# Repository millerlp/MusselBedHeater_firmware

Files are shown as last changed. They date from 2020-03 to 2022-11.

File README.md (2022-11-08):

# MusselBedHeater_firmware
Luke Miller, 2020

A permanent archive of this repository is stored in a Zenodo archive: https://doi.org/10.5281/zenodo.7246441 

 Firmware and hardware for Mussel Bed Heater project that Claire Windecker carried out 
 for her Masters thesis at Cal Poly Humboldt. The project consists of a circuit board 
 design that uses Arduino software to control an ATmega328P microcontroller to carry out 
 temperature monitoring and control heated artificial mussel beds. 
 
MusselBedHeater circuit board diagram

## Hardware design files 

Hardware_files/ contains parts lists, bill of materials, and Autocad Eagle design files. MusselBedHeater_RevG is the
most recent version, and contains all of the modifications made to the Revision F boards that were used 
in the field experiment. The heater sub-assembly board is in Heater_subassembly_revA.

## Arduino software files 

library_copies/ contains copies of the necessary Arduino libraries used to run the MusselBedHeater_firmware

Arduino programs used to run the hardware in the field are contained in:
* MusselBedHeater_6Crise/
* MusselBedHeater_field/

Utility Arduino programs used to set up the boards initially are in:
* serial_number_generator/
* settime_Serial/

### Reference mussels

Part of the design included the need to have a reference temperature, which the heated mussels would then 
be heated above by 2C or 6C. Reference mussels used a MAX31820 OneWire temperature sensor, which was 
embedded in artificial epoxy mussels as well. One control board can monitor 4 reference temperature sensors. 
The software averages the temperatures from the available reference mussels and uses that value to establish
the 'ambient' mussel temperature. Heated mussels were then heated to a target temperature increase, 2 or 6 degrees
Celsius above ambient. 

A TO-92 package MAX31820 is shown wired into the cable that will lead back to the battery box and controller board.
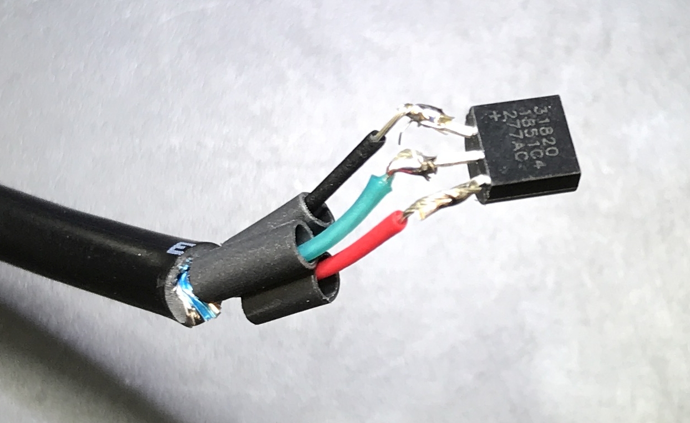
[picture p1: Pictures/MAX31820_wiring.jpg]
MAX31820 sensor wiring


## Heating assembly 

The heated artificial mussels were built using 38 Gauge Nichrome 80 wire (14 ohm per meter) in a 
length of 300 mm (~12 inches) wrapped around the Heater_subassembly_revA circuit board. This arrangement
should consume a maximum of about 3 Watts at 13V supply, but the circuit board is designed to pulse width
modulate the supply voltage to the heater and provide a basic PID control algorithm to achieve a desired 
target temperature above ambient. 

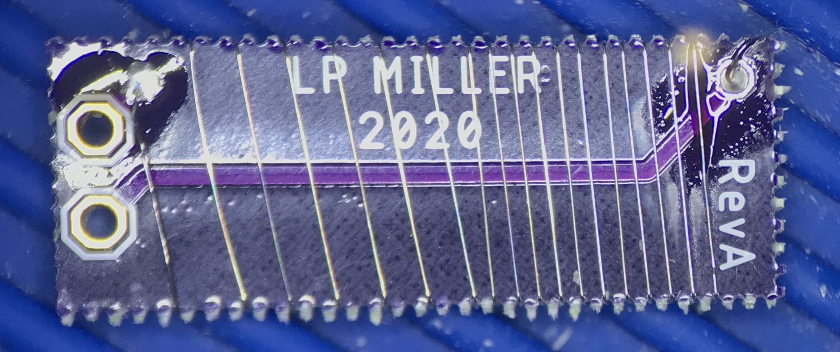
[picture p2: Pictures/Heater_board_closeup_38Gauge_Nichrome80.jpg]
Subassembly board


The cable supplying power to the heater coil also connected to a 6800 ohm 3% NTC thermistor, which was
used to measure the temperature of the artificial mussel. The thermistor was wired in a half-bridge
configured with 4700 ohm precision resistors found on the main MusselBedHeater_RevG circuit board.

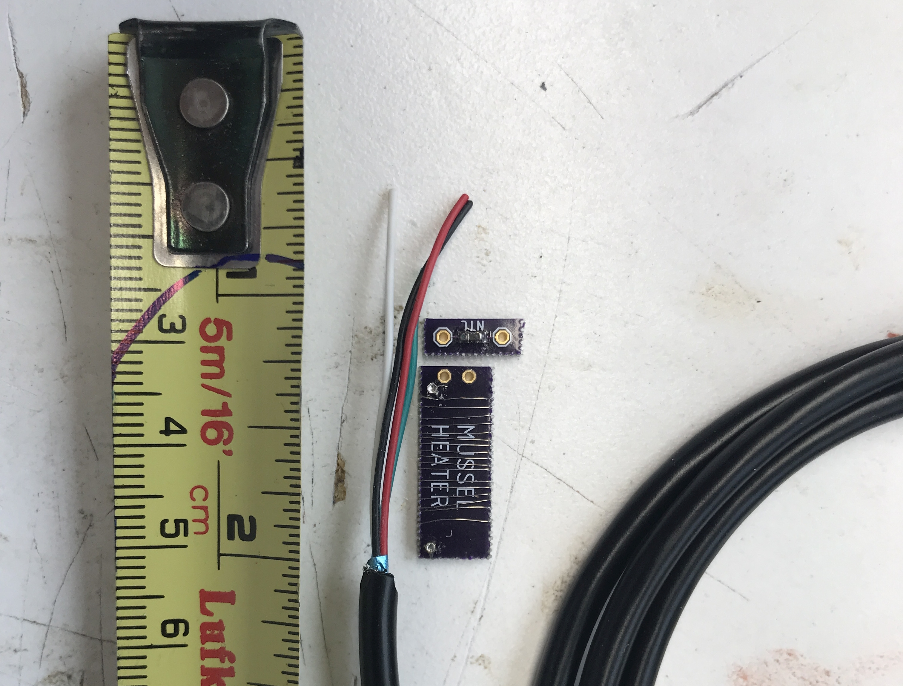
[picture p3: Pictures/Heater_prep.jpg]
Thermistor and heater coil board


The thermistor and heater coil board were eventually cast into the middle of an epoxy artificial mussel. 

One control board can control up to 16 heated mussels, including measuring their thermistor temperatures.

## Acknowledgements 
Funding from the National Science Foundation grants OCE-1904184 and OCE-1904185 helped support Luke Miller 
during the development of this hardware and software.

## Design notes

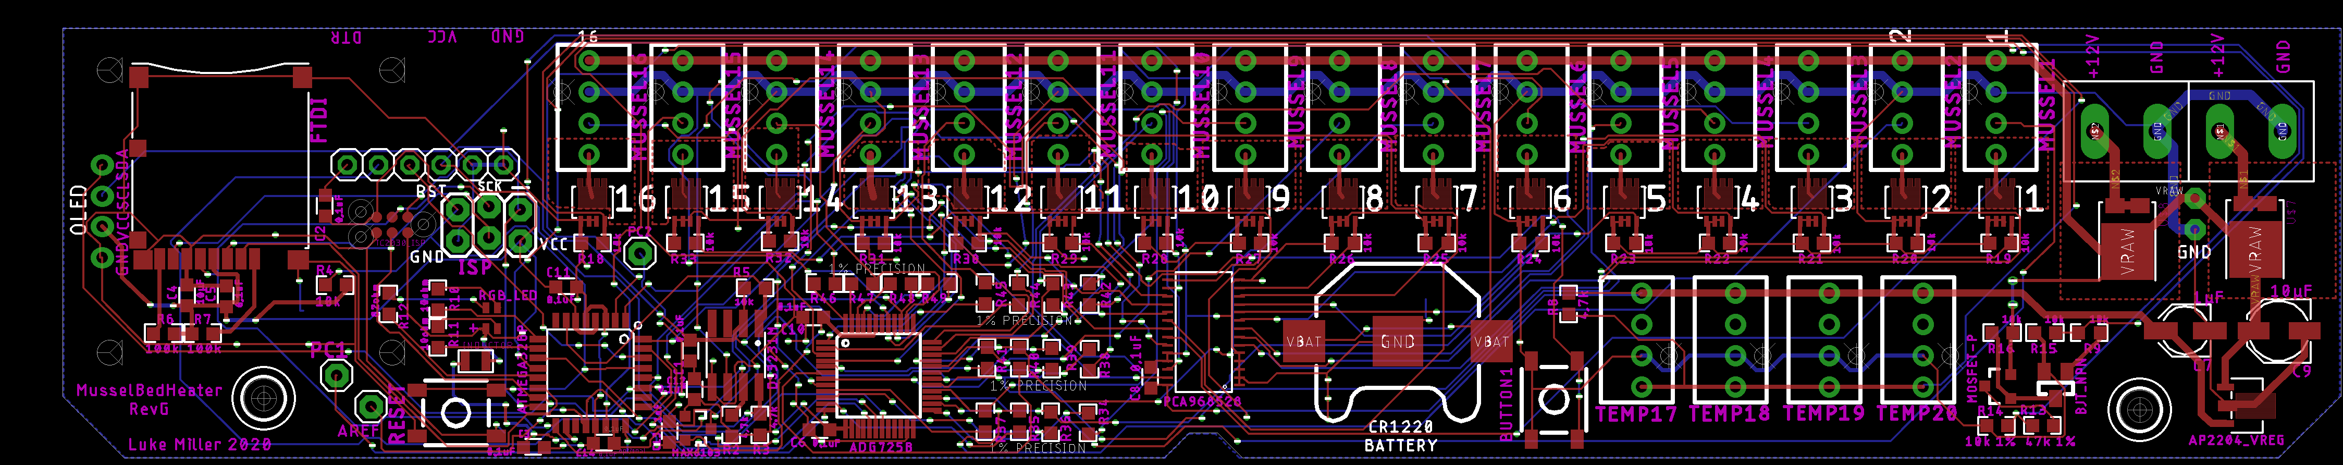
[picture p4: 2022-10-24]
Hardware_files/Eagle_files/MusselBedHeater_RevG_board.png

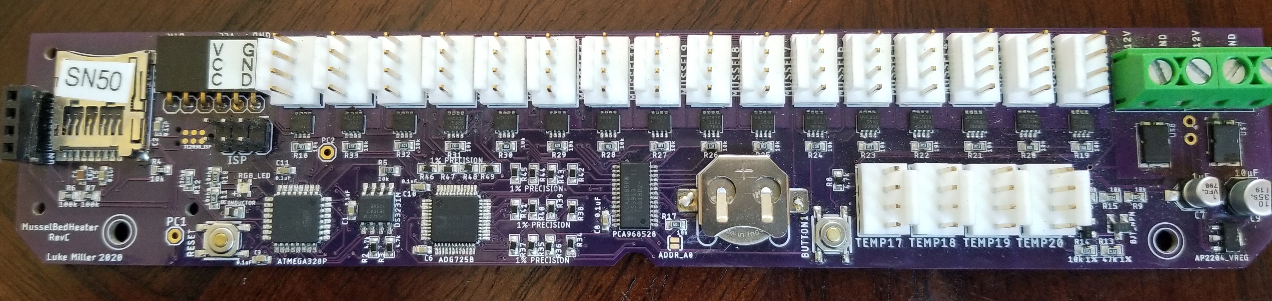
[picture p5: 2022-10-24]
Pictures/20210609_122934_RevE.jpg

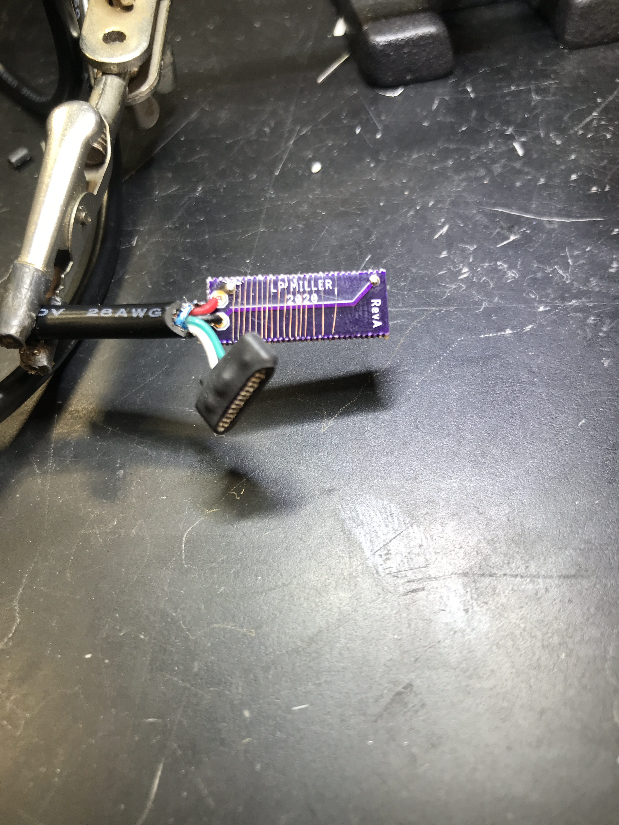
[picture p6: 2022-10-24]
Pictures/Heater_and_thermistor_finished.jpg

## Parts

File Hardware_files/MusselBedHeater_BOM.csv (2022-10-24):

Revision F, G MusselBedHeater
Qty | Value | Device | Package | Parts
1 |  | PINHD-1X6RA | 1X06-RIGHT_ANGLE | FTDI
10 | 0.1uF | CAP0603 | 0603 | C1, C2, C3, C5, C6, C8, C10, C11, C12, C14
2 | 100k 5% | RESISTOR_SMDR0603 | R0603 | R6, R7
21 | 10k 5% | RESISTOR_SMDR0603 | R0603 | R4, R5, R9, R15, R16, R18, R19, R20, R21, R22, R23, R24, R25, R26, R27, R28, R29, R30, R31, R32, R33
1 | 10k 1% or 0.5% | RESISTOR_SMDR0603 (battery reference) | R0603 | R14
2 | 10 ohm | RESISTOR_SMDR0603 (LED) | R0603 | R10, R11
1 | 10 µF | CAP0603 | 0603 | C4
1 | 10 µF | CPOL-USC | PANASONIC_C | C9
1 | 1uF | CAP0603 | 0603 | C13
1 | 1µF | CPOL-USB | PANASONIC_B | C7
3 | 4.7k 5% | RESISTOR_SMDR0603 (pull-ups) | R0603 | R2, R3, R8
16 | 4.7 kohm 1% | RESISTOR_SMDR0603 (thermistor ref) | R0603 | R34, R35, R36, R37, R38, R39, R40, R41, R42, R43, R44, R45, R46, R47, R48, R49
1 | 47k 1% or 0.5% | RESISTOR_SMDR0603 (battery reference) | R0603 | R13
1 | 82 ohm | RESISTOR_SMDR0603 (LED) | R0603 | R12
1 | ADG725_MUX | ADG725_MUX | TQFP48 | ADG725B
1 | AP2204R | AP2204R Voltage regulator | SOT-89 | AP2204_VREG
1 | ATMEGA328P | ATMEGA328_SMT | TQFP32-08 | ATMEGA328P
1 | AVR_SPI_PRG_62X3_LOCK | 2x3 header 0.1" pitch | 2X3_LOCK | ISP
1 | BATTERY_BUTTON_CELLCR1220_SMD | BATTERY_BUTTON_CELLCR1220_SMD | CR1220_BATTERY_HOLDER_SMD | U$5
1 | BJT_NPN_FMMT619TA | BJT_NPN_FMMT619TA (battery monitor) | SOT23 | BJT_NPN
1 | MOSFET-PCHANNELBSH203 | MOSFET-PCHANNELBSH203 (battery monitor) | SOT23-3 | MOSFET-P
1 | DS3231MSOIC-8 | DS3231MSOIC-8 (real time clock) | DS3231M_SOIC8 | DS3231M
1 | INDUCTOR0805_TY | INDUCTOR0805_TY | I_0805 | INDUCTOR
1 | LED_3_COLOR_ANODE1 | LED_3_COLOR_ANODE1 | LED_RGB_SMD_1.6X1.6 | RGB_LED
1 | MAX6100-MAX6107_VOLTAGE_REF | MAX6100-MAX6107_VOLTAGE_REF | SOT23-3 | MAX6103
1 | MICROSD_MOLEX_REVERSECURRENT | MICROSD_MOLEX_REVERSECURRENT | MICROSD_SOCKET_MOLEX_REVERSEMOUNT | U$2
16 | MOSFET-N_LFPAK33 | MOSFET-N_LFPAK33 | SOT1210 | U$10, U$11, U$12, U$13, U$14, U$15, U$16, U$17, U$18, U$19, U$20, U$21, U$22, U$23, U$24, U$25
1 | OLED_0.96_I2CGND_PIN1_WIDE | 4-pin 0.1" pitch header | OLED_0.96_I2C_GND_PIN1_WIDE | OLED
1 | PCA968528 | PCA968528 | 28-TSSOP | PCA9685
2 | PUSHBUTTON_DPST_SMD2SMALL | PUSHBUTTON_DPST_SMD2SMALL | PUSHBUTTON_SPST_PTS525_SERIES | BUTTON1, RESET
2 | SCHOTTKY_DIODE_TO-277-3 | SCHOTTKY_DIODE_TO-277-3 | TO-277-3 | U$7, U$8
2 | TERMINAL-2PIN-5.08MMLARGEHOLE | TERMINAL-2PIN-5.08MMLARGEHOLE | TERMINAL-2PIN-5.08MM_LARGEHOLE | BATT_INPUT1, BATT_INPUT2

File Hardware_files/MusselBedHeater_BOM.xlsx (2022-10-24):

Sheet: RevF-G
Revision F, G MusselBedHeater
Qty | Value | Device | Package | Parts
1 |  | PINHD-1X6RA | 1X06-RIGHT_ANGLE | FTDI
10 | 0.1uF | CAP0603 | 0603 | C1, C2, C3, C5, C6, C8, C10, C11, C12, C14
2 | 100k 5% | RESISTOR_SMDR0603 | R0603 | R6, R7
21 | 10k 5% | RESISTOR_SMDR0603 | R0603 | R4, R5, R9, R15, R16, R18, R19, R20, R21, R22, R23, R24, R25, R26, R27, R28, R29, R30, R31, R32, R33
1 | 10k 1% or 0.5% | RESISTOR_SMDR0603 (battery reference) | R0603 | R14
2 | 10 ohm | RESISTOR_SMDR0603 (LED) | R0603 | R10, R11
1 | 10 µF | CAP0603 | 0603 | C4
1 | 10 µF | CPOL-USC | PANASONIC_C | C9
1 | 1uF | CAP0603 | 0603 | C13
1 | 1µF | CPOL-USB | PANASONIC_B | C7
3 | 4.7k 5% | RESISTOR_SMDR0603 (pull-ups) | R0603 | R2, R3, R8
16 | 4.7 kohm 1% | RESISTOR_SMDR0603 (thermistor ref) | R0603 | R34, R35, R36, R37, R38, R39, R40, R41, R42, R43, R44, R45, R46, R47, R48, R49
1 | 47k 1% or 0.5% | RESISTOR_SMDR0603 (battery reference) | R0603 | R13
1 | 82 ohm | RESISTOR_SMDR0603 (LED) | R0603 | R12
1 | ADG725_MUX | ADG725_MUX | TQFP48 | ADG725B
1 | AP2204R | AP2204R Voltage regulator | SOT-89 | AP2204_VREG
1 | ATMEGA328P | ATMEGA328_SMT | TQFP32-08 | ATMEGA328P
1 | AVR_SPI_PRG_62X3_LOCK | 2x3 header 0.1" pitch | 2X3_LOCK | ISP
1 | BATTERY_BUTTON_CELLCR1220_SMD | BATTERY_BUTTON_CELLCR1220_SMD | CR1220_BATTERY_HOLDER_SMD | U$5
1 | BJT_NPN_FMMT619TA | BJT_NPN_FMMT619TA (battery monitor) | SOT23 | BJT_NPN
1 | MOSFET-PCHANNELBSH203 | MOSFET-PCHANNELBSH203 (battery monitor) | SOT23-3 | MOSFET-P
1 | DS3231MSOIC-8 | DS3231MSOIC-8 (real time clock) | DS3231M_SOIC8 | DS3231M
1 | INDUCTOR0805_TY | INDUCTOR0805_TY | I_0805 | INDUCTOR
1 | LED_3_COLOR_ANODE1 | LED_3_COLOR_ANODE1 | LED_RGB_SMD_1.6X1.6 | RGB_LED
1 | MAX6100-MAX6107_VOLTAGE_REF | MAX6100-MAX6107_VOLTAGE_REF | SOT23-3 | MAX6103
1 | MICROSD_MOLEX_REVERSECURRENT | MICROSD_MOLEX_REVERSECURRENT | MICROSD_SOCKET_MOLEX_REVERSEMOUNT | U$2
16 | MOSFET-N_LFPAK33 | MOSFET-N_LFPAK33 | SOT1210 | U$10, U$11, U$12, U$13, U$14, U$15, U$16, U$17, U$18, U$19, U$20, U$21, U$22, U$23, U$24, U$25
1 | OLED_0.96_I2CGND_PIN1_WIDE | 4-pin 0.1" pitch header | OLED_0.96_I2C_GND_PIN1_WIDE | OLED
1 | PCA968528 | PCA968528 | 28-TSSOP | PCA9685
2 | PUSHBUTTON_DPST_SMD2SMALL | PUSHBUTTON_DPST_SMD2SMALL | PUSHBUTTON_SPST_PTS525_SERIES | BUTTON1, RESET
2 | SCHOTTKY_DIODE_TO-277-3 | SCHOTTKY_DIODE_TO-277-3 | TO-277-3 | U$7, U$8
2 | TERMINAL-2PIN-5.08MMLARGEHOLE | TERMINAL-2PIN-5.08MMLARGEHOLE | TERMINAL-2PIN-5.08MM_LARGEHOLE | BATT_INPUT1, BATT_INPUT2

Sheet: RevC
Exported from MusselBedHeater_RevC.sch 2020-03-09
Qty | Value | Device | Package | Parts
1 | Right angle 1x6 header | PINHD-1X6RA | 1X06-RIGHT_ANGLE | FTDI
2 | 100k 5% | RESISTOR_SMDR0603 | R0603 | R6, R7
22 | 10k 5% | RESISTOR_SMDR0603 | R0603 | R4, R5, R9, R15, R16, R17, R18, R19, R20, R21, R22, R23, R24, R25, R26, R27, R28, R29, R30, R31, R32, R33
1 | 10k 1% | RESISTOR_SMDR0603 | R0603 | R14
2 | 10ohm 5% | RESISTOR_SMDR0603 | R0603 | R10, R11
1 | 82ohm 5% | RESISTOR_SMDR0603 | R0603 | R12
8 | 0.1uF | CAP0603 | 603 | C1, C2, C3, C5, C6, C8, C10, C11
1 | 10µF | CAP0603 | 603 | C4
1 | 10µF | CPOL-USC | PANASONIC_C | C9
1 | 1µF | CPOL-USB | PANASONIC_B | C7
3 | 4.7k 5% | RESISTOR_SMDR0603 | R0603 | R2, R3, R8
16 | Rref_1% (4.7kohm) | RESISTOR_SMDR0603 | R0603 | R34, R35, R36, R37, R38, R39, R40, R41, R42, R43, R44, R45, R46, R47, R48, R49
1 | 47k 1% | RESISTOR_SMDR0603 | R0603 | R13
1 | ADG725_MUX | ADG725_MUX | TQFP48 | ADG725B
1 | AP2204R | AP2204R | SOT-89 | AP2204_VREG
1 | ATMEGA328P | ATMEGA328_SMT | TQFP32-08 | ATMEGA328P
1 | AVR_SPI_PRG_62X3_LOCK | AVR_SPI_PRG_62X3_LOCK | 2X3_LOCK | ISP
1 | BATTERY_BUTTON_CELLCR1220_SMD | BATTERY_BUTTON_CELLCR1220_SMD | CR1220_BATTERY_HOLDER_SMD | U$5
1 | BJT_NPN_FMMT619TA | BJT_NPN_FMMT619TA | SOT23 | BJT_NPN
1 | DS3231MSOIC-8 | DS3231MSOIC-8 | DS3231M_SOIC8 | DS3231M
2 | HOLE-LAYOUT4-40-SOCKET-HEAD | HOLE-LAYOUT4-40-SOCKET-HEAD | 4-40-SCREW-HOLE | H1, H2
1 | INDUCTOR0805_TY | INDUCTOR0805_TY | I_0805 | INDUCTOR
1 | LED_3_COLOR_ANODE1 | LED_3_COLOR_ANODE1 | LED_RGB_SMD_1.6X1.6 | RGB_LED
1 | MICROSD_MOLEX_REVERSECURRENT | MICROSD_MOLEX_REVERSECURRENT | MICROSD_SOCKET_MOLEX_REVERSEMOUNT | U$2
20 | MOLEX_KK_254_4_PIN_HEADER | MOLEX_KK_254_4_PIN_HEADER | MOLEX_KK_254_4PIN_HEADER | MUSSEL 1-16, TEMP 17-20
16 | MOSFET-N_LFPAK33 | MOSFET-N_LFPAK33 | SOT1210 | U$10, U$11, U$12, U$13, U$14, U$15, U$16, U$17, U$18, U$19, U$20, U$21, U$22, U$23, U$24, U$25
1 | MOSFET-PCHANNELBSH203 | MOSFET-PCHANNELBSH203 | SOT23-3 | MOSFET-P
1 | OLED_0.96_I2CGND_PIN1_WIDE | OLED_0.96_I2CGND_PIN1_WIDE | OLED_0.96_I2C_GND_PIN1_WIDE | OLED
1 | PAD_SMD_1X1SMD* | PAD_SMD_1X1SMD* | SMD_PAD_1.6X0.8 | ADC6
1 | PCA968528 | PCA968528 | 28-TSSOP | PCA9685
2 | PINHD-1X1STANDARD | PINHD-1X1STANDARD | 1X01 | PC1, PC2
1 | PINHD-1X2NOSILK | PINHD-1X2NOSILK | 1X02_NOSILK | VRAW_TEST
2 | PUSHBUTTON_DPST_SMD2SMALL | PUSHBUTTON_DPST_SMD2SMALL | PUSHBUTTON_SPST_PTS525_SERIES | BUTTON1, RESET
2 | SCHOTTKY_DIODE_TO-277-3 | SCHOTTKY_DIODE_TO-277-3 | TO-277-3 | U$7, U$8
2 | TERMINAL-2PIN-5.08MMLARGEHOLE | TERMINAL-2PIN-5.08MMLARGEHOLE | TERMINAL-2PIN-5.08MM_LARGEHOLE | BATT_INPUT1, BATT_INPUT2

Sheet: RevD
Exported from MusselBedHeater_RevD_bom.csv 2020-05-23
Qty | Value | Device | Package | Parts
1 |  | PINHD-1X6RA | 1X06-RIGHT_ANGLE | FTDI
10 | 0.1uF | CAP0603 | 603 | C1, C2, C3, C5, C6, C8, C10, C11, C12, C14
2 | 100k | RESISTOR_SMDR0603 | R0603 | R6, R7
22 | 10k | RESISTOR_SMDR0603 | R0603 | R1, R4, R5, R9, R15, R16, R18, R19, R20, R21, R22, R23, R24, R25, R26, R27, R28, R29, R30, R31, R32, R33
1 | 10k 1% | RESISTOR_SMDR0603 | R0603 | R14
2 | 10ohm | RESISTOR_SMDR0603 | R0603 | R10, R11
1 | 10µF | CAP0603 | 603 | C4
1 | 10µF | CPOL-USC | PANASONIC_C | C9
1 | 1uF | CAP0603 | 603 | C13
1 | 1µF | CPOL-USB | PANASONIC_B | C7
3 | 4.7k | RESISTOR_SMDR0603 | R0603 | R2, R3, R8
1 | 47k 1% | RESISTOR_SMDR0603 | R0603 | R13
1 | 82ohm | RESISTOR_SMDR0603 | R0603 | R12
1 | ADG725_MUX | ADG725_MUX | TQFP48 | ADG725B
1 | AP2204R | AP2204R | SOT-89 | AP2204_VREG
1 | ATMEGA_3209_4809_48PINTQFP | ATMEGA_3209_4809_48PINTQFP | TQFP48_ATMEL_MICROCHIP | U$1
1 | ATMEL_UPDI_PROGRAMMER100MIL | ATMEL_UPDI_PROGRAMMER100MIL | 2X3 | U$3
1 | BATTERY_BUTTON_CELLCR1220_SMD | BATTERY_BUTTON_CELLCR1220_SMD | CR1220_BATTERY_HOLDER_SMD | U$5
1 | BJT_NPN_FMMT619TA | BJT_NPN_FMMT619TA | SOT23 | BJT_NPN
1 | DS3231MSOIC-8 | DS3231MSOIC-8 | DS3231M_SOIC8 | DS3231M
2 | HOLE-LAYOUT4-40-SOCKET-HEAD | HOLE-LAYOUT4-40-SOCKET-HEAD | 4-40-SCREW-HOLE | H1, H2
1 | INDUCTOR0805_TY | INDUCTOR0805_TY | I_0805 | INDUCTOR
1 | LED_3_COLOR_ANODE1 | LED_3_COLOR_ANODE1 | LED_RGB_SMD_1.6X1.6 | RGB_LED
1 | MAX6100-MAX6107_VOLTAGE_REF | MAX6100-MAX6107_VOLTAGE_REF | SOT23-3 | MAX6103
1 | MICROSD_MOLEX_REVERSECURRENT | MICROSD_MOLEX_REVERSECURRENT | MICROSD_SOCKET_MOLEX_REVERSEMOUNT | U$2
20 | MOLEX_KK_254_4_PIN_HEADER | MOLEX_KK_254_4_PIN_HEADER | MOLEX_KK_254_4PIN_HEADER | MUSSEL 1-16, TEMP 17-20
16 | MOSFET-N_LFPAK33 | MOSFET-N_LFPAK33 | SOT1210 | U$10, U$11, U$12, U$13, U$14, U$15, U$16, U$17, U$18, U$19, U$20, U$21, U$22, U$23, U$24, U$25
1 | MOSFET-PCHANNELBSH203 | MOSFET-PCHANNELBSH203 | SOT23-3 | MOSFET-P
1 | OLED_0.96_I2CGND_PIN1_WIDE | OLED_0.96_I2CGND_PIN1_WIDE | OLED_0.96_I2C_GND_PIN1_WIDE | OLED
2 | PAD_SMD_1X1SMD* | PAD_SMD_1X1SMD* | SMD_PAD_1.6X0.8 | ADC1, ADC6
1 | PCA968528 | PCA968528 | 28-TSSOP | PCA9685
2 | PINHD-1X1STANDARD | PINHD-1X1STANDARD | 1X01 | PC3, PC4
1 | PINHD-1X2NOSILK | PINHD-1X2NOSILK | 1X02_NOSILK | VRAW_TEST
2 | PUSHBUTTON_DPST_SMD2SMALL | PUSHBUTTON_DPST_SMD2SMALL | PUSHBUTTON_SPST_PTS525_SERIES | BUTTON1, RESET
16 | Rref_1% | RESISTOR_SMDR0603 | R0603 | R34, R35, R36, R37, R38, R39, R40, R41, R42, R43, R44, R45, R46, R47, R48, R49
2 | SCHOTTKY_DIODE_TO-277-3 | SCHOTTKY_DIODE_TO-277-3 | TO-277-3 | U$7, U$8
2 | TERMINAL-2PIN-5.08MMLARGEHOLE | TERMINAL-2PIN-5.08MMLARGEHOLE | TERMINAL-2PIN-5.08MM_LARGEHOLE | BATT_INPUT1, BATT_INPUT2

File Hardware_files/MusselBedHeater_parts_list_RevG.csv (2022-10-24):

Digikey.com materials | Manufacturer PN | Digikey PN | Qty | Unit Price | Per-board price | PCB Identifiers | Alternative part | Alternative PN | Alternative Digikey
AVR ATMEGA328P-AU 32 PIN TQFP surface mount |  | ATMEGA328P-AU-ND | 1 | $3.61 | $3.61 | ATMEGA328P
CR1220 battery slot, surface mount | 3000 | 36-3000-ND | 1 | $0.56 | $0.56 | U$5
CR1220 battery | ECR1220 | N739-ND | 1 | $1.11 | $1.11
DS3231M real time clock 8-SOIC | DS3231MZ+ | DS3231MZ+-ND | 1 | $7.69 | $7.69 | DS3231M
Voltage regulator, 3.3V, SOT-89 (input up to 24V) | AP2204R-3.3TRG1 | AP2204R-3.3TRG1DICT-ND | 1 | $0.47 | $0.47 | AP2204_VREG
Voltage reference - MAX6103 3.0V | MAX6103EUR+T | MAX6103EUR+TCT-ND | 1 | $1.19 | $1.19 | MAX6103
pushbutton surface mount (small, 1.5mm height) | PTS525SM15SMTR2 LFS | CKN9104CT-ND | 2 | $0.33 | $0.66 | BUTTON1, RESET
Capacitor 0.1uF - 0603 ceramic 25V | CL10A104KA8NNNC | 1276-1857-6-ND | 7 | $0.10 | $0.70 | C1, C2, C3, C5, C6, C8, C10, C11, C12, C14
Capacitor, 1uF, 0603 ceramic 16V, X7R | CL10B105MO8NNWC | 1276-6524-1-ND | 1 | $0.10 | $0.10 | C13
Capacitor 10uF - 0603 ceramic 25V | GRM188R61C106KAALJ | 490-12736-1-ND | 1 | $0.43 | $0.43 | C4
Capacitor, surface mount 1uF 35V, electrolytic, Panasonic FC series, size code B (for Voltage reg) | EEE-FC1V1R0R | PCE4024CT-ND | 1 | $0.46 | $0.46 | C7
Capacitor, surface mount 10uF 35V, electrolytic, Panasonic S series, Type V, 5mm size Code C (for Voltage reg) | EEE-1VA100SR | PCE3947CT-ND | 1 | $0.29 | $0.29 | C9
PCA9685 16-channel PWM expander | PCA9685PW/Q900,118 | 568-5931-1-ND | 1 | $2.46 | $2.46 | PCA9685
N-channel MOSFET (to turn on heater)LFPAK33, 30V, 50A | PSMN9R8-30MLC,115 | 1727-7146-1-ND | 16 | $0.43 | $6.80 | U$10, U$11, U$12, U$13, U$14, U$15, U$16, U$17, U$18, U$19, U$20, U$21, U$22, U$23, U$24, U$25
Schottky diode - 20A 80V TO-277-3 | TSPB20U80S S1G | TSPB20U80SS1GCT-ND | 2 | $1.06 | $2.12 | U$7, U$8
MAX31820 temperature sensor | MAX31820MCR+ | MAX31820MCR+-ND | 4 | $1.65 | $6.60
ADG725B dual channel 16:1 multiplexer | ADG725BSUZ | ADG725BSUZ-ND | 1 | $12.64 | $12.64 | ADG725B
Thermistor Panasonic 6800k 3% tolerance, size 0603 | ERT-J1VR682H | P124035CT-ND | 16 | $0.29 | $4.64
microSD terminal Molex | 5027740891 | WM24066CT-ND | 1 | $3.47 | $3.47 | U$2
Molex KK male 4-pin connector thru-hole | 22112042 | WM2702-ND | 20 | $0.55 | $10.94
Molex KK female 4-pin connector | 10112043 | WM2603-ND | 20 | $0.18 | $3.68
Molex KK crimp-on connector 24-30AWG | 469990101 | WM5268-ND | 90 | $0.19 | $17.35
3-color LED RGB, Kingbright | APTF1616SEEZGKQBKC | 754-1977-1-ND | 1 | $0.92 | $0.92 | RGB_LED
Resistor 10 ohm for green,blue LED legs 0603 | ERJ-3GEYJ100V | P10GCT-ND | 2 | $0.10 | $0.20 | R10, R11
Resistor 82 ohm for red LED leg 0603 | ERJ-3GEYJ820V | P82GCT-ND | 1 | $0.10 | $0.10 | R12
Resistor 4.7 kohm I2C pullups, DS18B20 0603 | ERJ-3GEYJ472V | P4.7KGCT-ND | 3 | $0.10 | $0.30 | R2, R3, R8
Resistor 4.7 kohm, 1% tolerance, 0603 (thermistor reference) | ERJ-PA3F4701V | P4.7KBYCT-ND | 16 | $0.14 | $2.24 | R34, R35, R36, R37, R38, R39, R40, R41, R42, R43, R44, R45, R46, R47, R48, R49
Resistor 10k 5% (generic pullup/pulldown) 0603 | ERJ-3GEYJ103V | P10KGCT-ND | 22 | $0.10 | $2.20 | R4, R5, R9, R15, R16, R18, R19, R20, R21, R22, R23, R24, R25, R26, R27, R28, R29, R30, R31, R32, R33
Resistor 10k 0.5% (battery monitor) 0603 | ERA-3AED103V | P123734CT-ND | 1 | $0.11 | $0.11 | R14
Resistor 47k 0.5% (battery monitor) 0603 | ERA-3AED473V | P123906CT-ND | 1 | $0.12 | $0.12 | R13
Resistor 100k (SD card pullup) 0603 | ERJ-3GEYJ104V | P100KGCT-ND | 2 | $0.10 | $0.20 | R6, R7
Inductor, 10µH 150mA, 360 mOhm | LBR2012T100K | 587-2045-1-ND | 1 | $0.11 | $0.11 | INDUCTOR
2x3 0.1" header - for ICSP + SPI connection | 961206-6404-AR | 3M9459-ND | 1 | $0.58 | $0.58 | ISP
4-conductor cable USB-2.0 28gauge 0.150" diameter, 50ft spool | 2725-2828-BL-01000-A | CN230B-50-ND | 1 | $14.61 | $14.61
BJT NPN Transistor 50V 2A SOT23-3 package (battery monitor) | FMMT619TA | FMMT619CT-ND | 1 | $0.50 | $0.50 | BJT_NPN | 2PD601ARL.215 NPN 50V 100mA | 2PD601ARL.215 | 1727-4147-1-ND
Mosfet P-FET SOT23-3 BH203,215 (battery monitor) | BSH203,215 | 1727-6216-1-ND | 1 | $0.38 | $0.38 | MOSFET-P
Hex Standoff Threaded #4-40 Aluminum 0.750" (19.05mm) 3/4" | 2108-440-AL | 1772-1777-ND | 2 | $0.38 | $0.76
#4-40 Pan Head Machine Screw Phillips Drive Stainless Steel, 3/8" length | 9901 | 36-9901-ND | 2 | $0.10 | $0.20
#4-40 Pan Head Machine Screw Phillips Drive Stainless Steel, 1/2" length | 9902 | 36-9902-ND | 2 | $0.13 | $0.26
#4 Flat Washer 0.062" (1.57mm) Thick Nylon | 16FW004062 | RPC6756-ND | 4 | $0.10 | $0.40
microSD card, 8GB (amazon etc.) |  |  | 1 | $8.28 | $8.28
Crimp connectors for battery tabs |  |  | 2 | $1.00 | $2.00
Wire for battery connector |  |  | 1 | $1.00 | $1.00
Printed circuit board, estimate per board |  |  | 1 | $17.00 | $17.00
Cable gland, 2.0-5mm cord diam, PG7 thread | IPG-2227 | 377-2183-ND | 20 | $0.55 | $11.00
Screw terminal (2-pin, 5.08mm spacing for connecting large wires) | EDZ250/2 | ED1973-ND | 2 | $1.20 | $2.40 | BATT_INPUT1, BATT_INPUT2
Total for 1 box - 16 mussels |  |  |  |  | $153.84
Total for 8 boxes |  |  |  |  | $1,538.42
Other parts:
Battery (2 per box x2 for quick-swapping) 12Ah - Miller has existing batteries | LC-RA1212P1 | P230-ND | 4 | $44.60 | $178.40
Seahorse SE-300 case for 2x 12Ah batteries - Miller has existing cases | SE-300 |  | 1 | $21.00 | $21.00

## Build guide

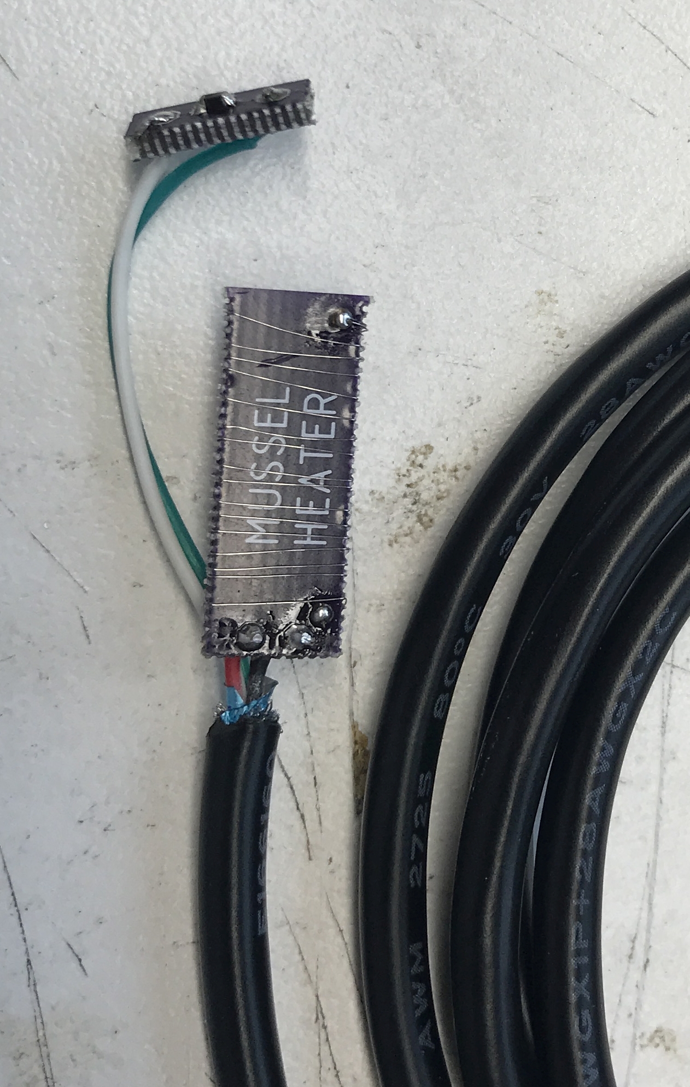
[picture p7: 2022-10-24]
Pictures/Heater_and_thermistor_soldered.jpg

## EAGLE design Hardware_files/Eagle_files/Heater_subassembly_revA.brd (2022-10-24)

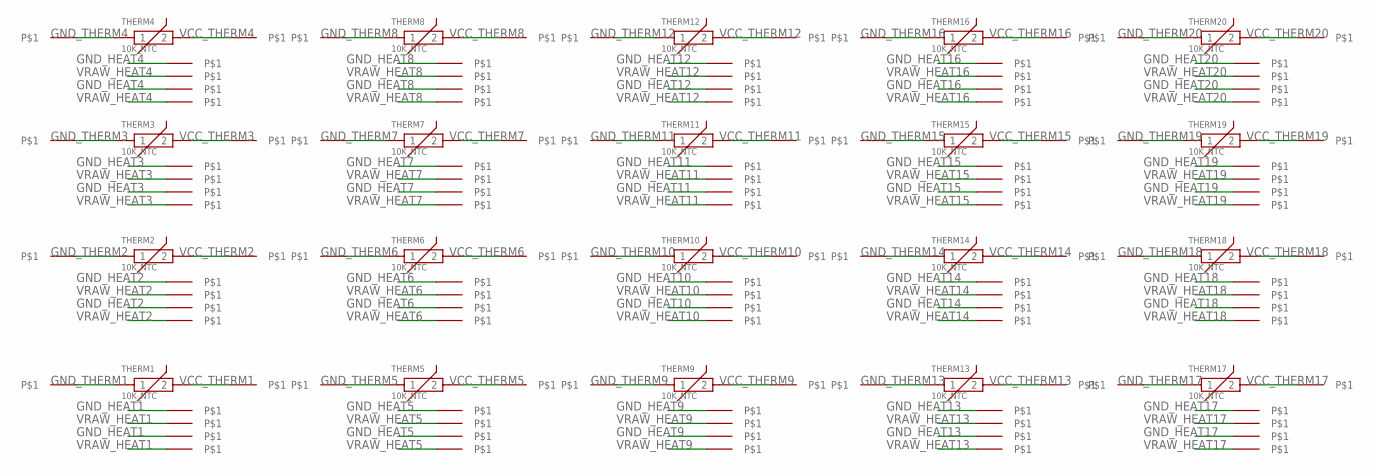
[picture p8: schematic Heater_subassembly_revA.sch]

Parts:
GND_HEAT1, GND_HEAT2, GND_HEAT3, GND_HEAT4, GND_HEAT5, GND_HEAT6, GND_HEAT7, GND_HEAT8, GND_HEAT9, GND_HEAT10, GND_HEAT11, GND_HEAT12, GND_HEAT13, GND_HEAT14, GND_HEAT15, GND_HEAT16, GND_HEAT17, GND_HEAT18, GND_HEAT19, GND_HEAT20: PINHD-1X1SMALL; 1X01_SMALL
GND_NICHROME1, GND_NICHROME2, GND_NICHROME3, GND_NICHROME4, GND_NICHROME5, GND_NICHROME6, GND_NICHROME7, GND_NICHROME8, GND_NICHROME9, GND_NICHROME10, GND_NICHROME11, GND_NICHROME12, GND_NICHROME13, GND_NICHROME14, GND_NICHROME15, GND_NICHROME16, GND_NICHROME17, GND_NICHROME18, GND_NICHROME19, GND_NICHROME20: PINHD-1X10.7MM_DRILL; 1X01_SMALL_0.7
GND_THERM1, GND_THERM2, GND_THERM3, GND_THERM4, GND_THERM5, GND_THERM6, GND_THERM7, GND_THERM8, GND_THERM9, GND_THERM10, GND_THERM11, GND_THERM12, GND_THERM13, GND_THERM14, GND_THERM16, GND_THERM17, GND_THERM18, GND_THERM19, GND_THERM20: PINHD-1X1SMALL; 1X01_SMALL
THERM1, THERM2, THERM3, THERM4, THERM5, THERM6, THERM7, THERM8, THERM9, THERM10, THERM11, THERM12, THERM13, THERM14, THERM15, THERM16, THERM17, THERM18, THERM19, THERM20: 10K_NTC; R0603_THERMISTOR
U$30: PINHD-1X1SMALL; 1X01_SMALL
VCC_THERM1, VCC_THERM2, VCC_THERM3, VCC_THERM4, VCC_THERM5, VCC_THERM6, VCC_THERM7, VCC_THERM8, VCC_THERM9, VCC_THERM10, VCC_THERM11, VCC_THERM12, VCC_THERM13, VCC_THERM14, VCC_THERM15, VCC_THERM16, VCC_THERM17, VCC_THERM18, VCC_THERM19, VCC_THERM20: PINHD-1X1SMALL; 1X01_SMALL
VRAW_HEAT1, VRAW_HEAT2, VRAW_HEAT3, VRAW_HEAT4, VRAW_HEAT5, VRAW_HEAT6, VRAW_HEAT7, VRAW_HEAT8, VRAW_HEAT9, VRAW_HEAT10, VRAW_HEAT11, VRAW_HEAT12, VRAW_HEAT13, VRAW_HEAT14, VRAW_HEAT15, VRAW_HEAT16, VRAW_HEAT17, VRAW_HEAT18, VRAW_HEAT19, VRAW_HEAT20: PINHD-1X1SMALL; 1X01_SMALL
VRAW_NICHROME1, VRAW_NICHROME2, VRAW_NICHROME3, VRAW_NICHROME4, VRAW_NICHROME5, VRAW_NICHROME6, VRAW_NICHROME7, VRAW_NICHROME8, VRAW_NICHROME9, VRAW_NICHROME10, VRAW_NICHROME11, VRAW_NICHROME12, VRAW_NICHROME13, VRAW_NICHROME14, VRAW_NICHROME15, VRAW_NICHROME16, VRAW_NICHROME17, VRAW_NICHROME18, VRAW_NICHROME19, VRAW_NICHROME20: PINHD-1X10.7MM_DRILL; 1X01_SMALL_0.7

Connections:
GND_HEAT1: GND_HEAT1.1, GND_NICHROME1.P$1
GND_HEAT2: GND_HEAT2.1, GND_NICHROME2.P$1
GND_HEAT3: GND_HEAT3.1, GND_NICHROME3.P$1
GND_HEAT4: GND_HEAT4.1, GND_NICHROME4.P$1
GND_HEAT5: GND_HEAT5.1, GND_NICHROME5.P$1
GND_HEAT6: GND_HEAT6.1, GND_NICHROME6.P$1
GND_HEAT7: GND_HEAT7.1, GND_NICHROME7.P$1
GND_HEAT8: GND_HEAT8.1, GND_NICHROME8.P$1
GND_HEAT9: GND_HEAT9.1, GND_NICHROME9.P$1
GND_HEAT10: GND_HEAT10.1, GND_NICHROME10.P$1
GND_HEAT11: GND_HEAT11.1, GND_NICHROME11.P$1
GND_HEAT12: GND_HEAT12.1, GND_NICHROME12.P$1
GND_HEAT13: GND_HEAT13.1, GND_NICHROME13.P$1
GND_HEAT14: GND_HEAT14.1, GND_NICHROME14.P$1
GND_HEAT15: GND_HEAT15.1, GND_NICHROME15.P$1
GND_HEAT16: GND_HEAT16.1, GND_NICHROME16.P$1
GND_HEAT17: GND_HEAT17.1, GND_NICHROME17.P$1
GND_HEAT18: GND_HEAT18.1, GND_NICHROME18.P$1
GND_HEAT19: GND_HEAT19.1, GND_NICHROME19.P$1
GND_HEAT20: GND_HEAT20.1, GND_NICHROME20.P$1
GND_THERM1: GND_THERM1.1, THERM1.1
GND_THERM2: GND_THERM2.1, THERM2.1
GND_THERM3: GND_THERM3.1, THERM3.1
GND_THERM4: GND_THERM4.1, THERM4.1
GND_THERM5: GND_THERM5.1, THERM5.1
GND_THERM6: GND_THERM6.1, THERM6.1
GND_THERM7: GND_THERM7.1, THERM7.1
GND_THERM8: GND_THERM8.1, THERM8.1
GND_THERM9: GND_THERM9.1, THERM9.1
GND_THERM10: GND_THERM10.1, THERM10.1
GND_THERM11: GND_THERM11.1, THERM11.1
GND_THERM12: GND_THERM12.1, THERM12.1
GND_THERM13: GND_THERM13.1, THERM13.1
GND_THERM14: GND_THERM14.1, THERM14.1
GND_THERM15: THERM15.1, U$30.1
GND_THERM16: GND_THERM16.1, THERM16.1
GND_THERM17: GND_THERM17.1, THERM17.1
GND_THERM18: GND_THERM18.1, THERM18.1
GND_THERM19: GND_THERM19.1, THERM19.1
GND_THERM20: GND_THERM20.1, THERM20.1
VCC_THERM1: THERM1.2, VCC_THERM1.1
VCC_THERM2: THERM2.2, VCC_THERM2.1
VCC_THERM3: THERM3.2, VCC_THERM3.1
VCC_THERM4: THERM4.2, VCC_THERM4.1
VCC_THERM5: THERM5.2, VCC_THERM5.1
VCC_THERM6: THERM6.2, VCC_THERM6.1
VCC_THERM7: THERM7.2, VCC_THERM7.1
VCC_THERM8: THERM8.2, VCC_THERM8.1
VCC_THERM9: THERM9.2, VCC_THERM9.1
VCC_THERM10: THERM10.2, VCC_THERM10.1
VCC_THERM11: THERM11.2, VCC_THERM11.1
VCC_THERM12: THERM12.2, VCC_THERM12.1
VCC_THERM13: THERM13.2, VCC_THERM13.1
VCC_THERM14: THERM14.2, VCC_THERM14.1
VCC_THERM15: THERM15.2, VCC_THERM15.1
VCC_THERM16: THERM16.2, VCC_THERM16.1
VCC_THERM17: THERM17.2, VCC_THERM17.1
VCC_THERM18: THERM18.2, VCC_THERM18.1
VCC_THERM19: THERM19.2, VCC_THERM19.1
VCC_THERM20: THERM20.2, VCC_THERM20.1
VRAW_HEAT1: VRAW_HEAT1.1, VRAW_NICHROME1.P$1
VRAW_HEAT2: VRAW_HEAT2.1, VRAW_NICHROME2.P$1
VRAW_HEAT3: VRAW_HEAT3.1, VRAW_NICHROME3.P$1
VRAW_HEAT4: VRAW_HEAT4.1, VRAW_NICHROME4.P$1
VRAW_HEAT5: VRAW_HEAT5.1, VRAW_NICHROME5.P$1
VRAW_HEAT6: VRAW_HEAT6.1, VRAW_NICHROME6.P$1
VRAW_HEAT7: VRAW_HEAT7.1, VRAW_NICHROME7.P$1
VRAW_HEAT8: VRAW_HEAT8.1, VRAW_NICHROME8.P$1
VRAW_HEAT9: VRAW_HEAT9.1, VRAW_NICHROME9.P$1
VRAW_HEAT10: VRAW_HEAT10.1, VRAW_NICHROME10.P$1
VRAW_HEAT11: VRAW_HEAT11.1, VRAW_NICHROME11.P$1
VRAW_HEAT12: VRAW_HEAT12.1, VRAW_NICHROME12.P$1
VRAW_HEAT13: VRAW_HEAT13.1, VRAW_NICHROME13.P$1
VRAW_HEAT14: VRAW_HEAT14.1, VRAW_NICHROME14.P$1
VRAW_HEAT15: VRAW_HEAT15.1, VRAW_NICHROME15.P$1
VRAW_HEAT16: VRAW_HEAT16.1, VRAW_NICHROME16.P$1
VRAW_HEAT17: VRAW_HEAT17.1, VRAW_NICHROME17.P$1
VRAW_HEAT18: VRAW_HEAT18.1, VRAW_NICHROME18.P$1
VRAW_HEAT19: VRAW_HEAT19.1, VRAW_NICHROME19.P$1
VRAW_HEAT20: VRAW_HEAT20.1, VRAW_NICHROME20.P$1

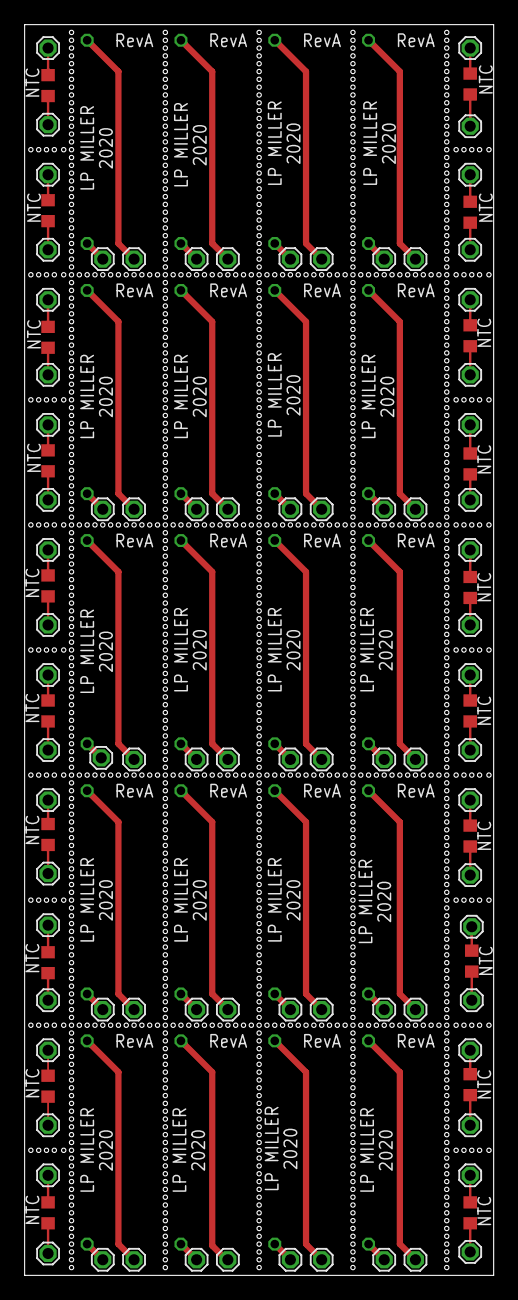
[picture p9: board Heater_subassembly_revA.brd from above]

Board: 2 copper layers, 38.1 x 101.6 mm, 140 parts (0 on the bottom side), 80 nets.

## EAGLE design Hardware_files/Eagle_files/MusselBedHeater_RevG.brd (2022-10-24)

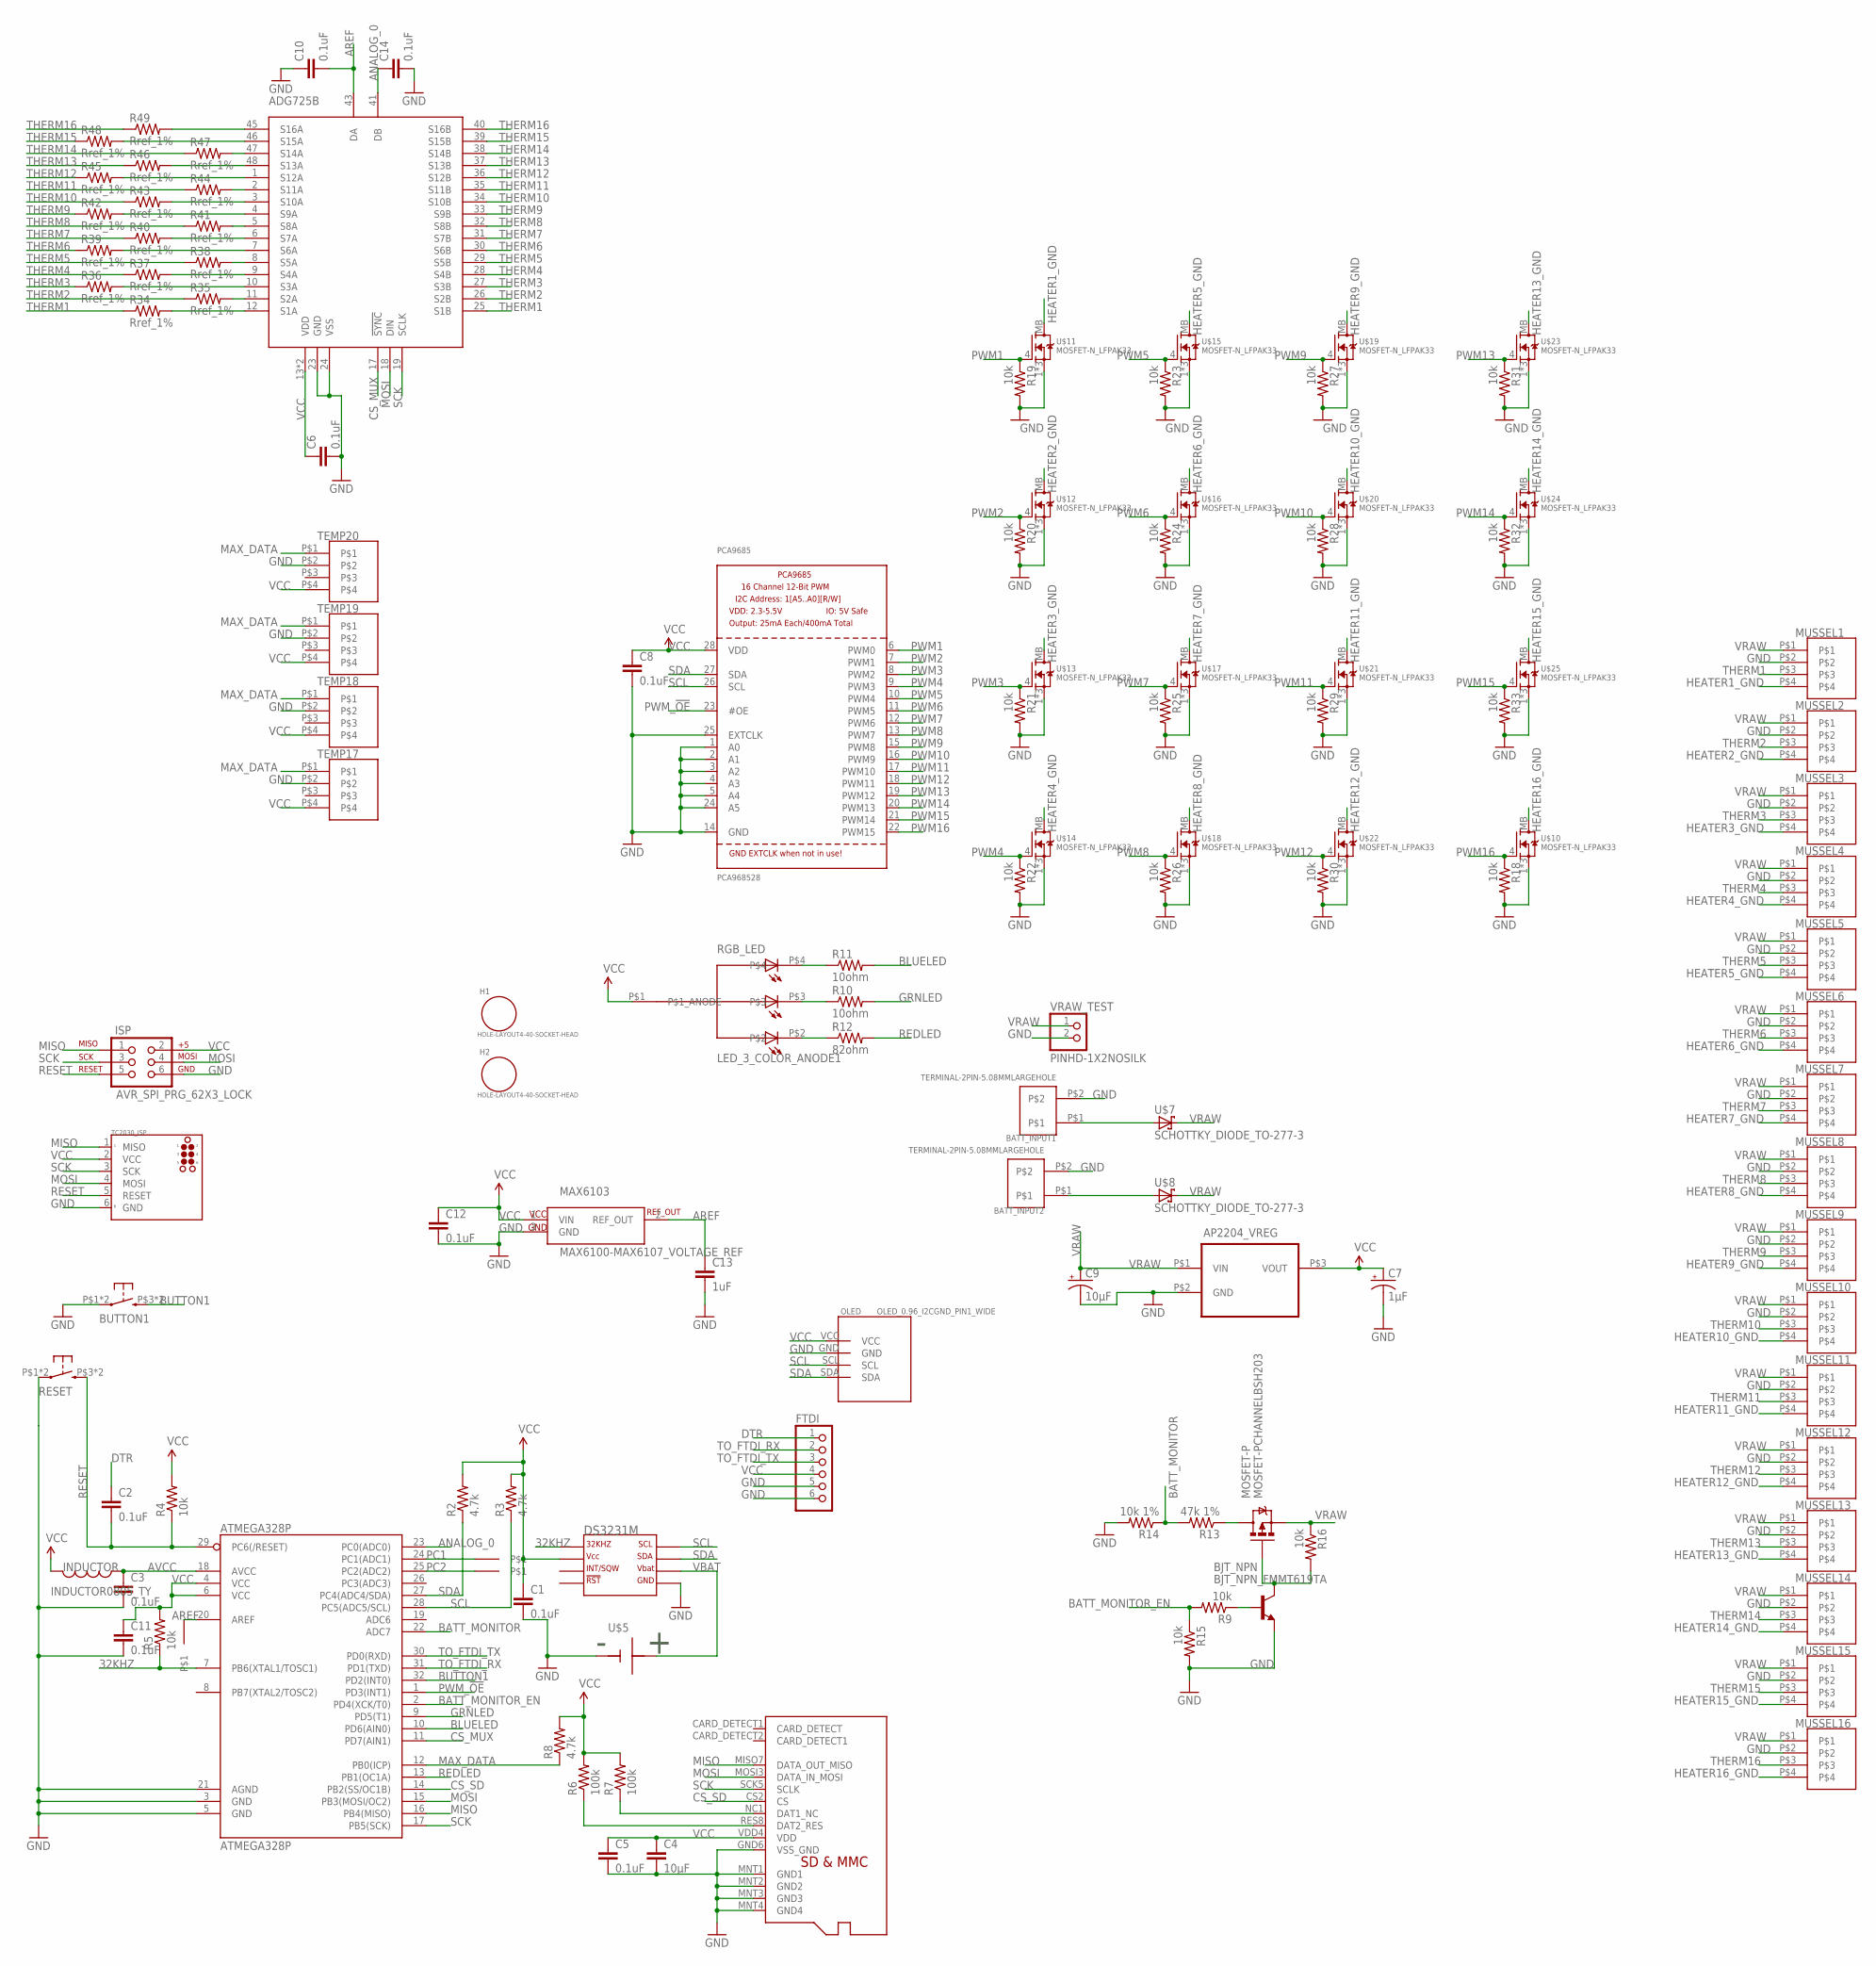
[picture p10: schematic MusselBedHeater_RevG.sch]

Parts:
ADG725B: ADG725_MUX; TQFP48
AP2204_VREG: AP2204R; SOT-89
AREF: PINHD-1X1STANDARD; 1X01
ATMEGA328P: ATMEGA328P; TQFP32-08
BATT_INPUT1, BATT_INPUT2: TERMINAL-2PIN-5.08MMLARGEHOLE; TERMINAL-2PIN-5.08MM_LARGEHOLE
BJT_NPN: BJT_NPN_FMMT619TA; SOT23
BUTTON1: PUSHBUTTON_DPST_SMD2SMALL; PUSHBUTTON_SPST_PTS525_SERIES
C1, C2, C3, C5, C6, C8, C10, C11, C12, C14: 0.1uF; 0603
C4: 10µF; 0603
C7: 1µF; PANASONIC_B
C9: 10µF; PANASONIC_C
C13: 1uF; 0603
DS3231M: DS3231MSOIC-8; DS3231M_SOIC8
FTDI: PINHD-1X6RA; 1X06-RIGHT_ANGLE
H1, H2: HOLE-LAYOUT4-40-SOCKET-HEAD; 4-40-SCREW-HOLE
INDUCTOR: INDUCTOR0805_TY; I_0805
ISP: AVR_SPI_PRG_62X3_LOCK; 2X3_LOCK
MAX6103: MAX6100-MAX6107_VOLTAGE_REF; SOT23-3
MOSFET-P: MOSFET-PCHANNELBSH203; SOT23-3
MUSSEL1, MUSSEL2, MUSSEL3, MUSSEL4, MUSSEL5, MUSSEL6, MUSSEL7, MUSSEL8, MUSSEL9, MUSSEL10, MUSSEL11, MUSSEL12, MUSSEL13, MUSSEL14, MUSSEL15, MUSSEL16: MOLEX_KK_254_4_PIN_HEADER; MOLEX_KK_254_4PIN_HEADER
OLED: OLED_0.96_I2CGND_PIN1_WIDE; OLED_0.96_I2C_GND_PIN1_WIDE
PC1, PC2: PINHD-1X1STANDARD; 1X01
PCA9685: PCA968528; 28-TSSOP
R2, R3, R8: 4.7k; R0603
R4, R5, R9, R15, R16, R18, R19, R20, R21, R22, R23, R24, R25, R26, R27, R28, R29, R30, R31, R32, R33: 10k; R0603
R6, R7: 100k; R0603
R10, R11: 10ohm; R0603
R12: 82ohm; R0603
R13: 47k 1%; R0603
R14: 10k 1%; R0603
R34, R35, R36, R37, R38, R39, R40, R41, R42, R43, R44, R45, R46, R47, R48, R49: Rref_1%; R0603
RESET: PUSHBUTTON_DPST_SMD2SMALL; PUSHBUTTON_SPST_PTS525_SERIES
RGB_LED: LED_3_COLOR_ANODE1; LED_RGB_SMD_1.6X1.6
TC2030_ISP: TC2030-MCP-NL
TEMP17, TEMP18, TEMP19, TEMP20: MOLEX_KK_254_4_PIN_HEADER; MOLEX_KK_254_4PIN_HEADER
U$2: MICROSD_MOLEX_REVERSECURRENT; MICROSD_SOCKET_MOLEX_REVERSEMOUNT
U$5: BATTERY_BUTTON_CELLCR1220_SMD; CR1220_BATTERY_HOLDER_SMD
U$7, U$8: SCHOTTKY_DIODE_TO-277-3; TO-277-3
U$10, U$11, U$12, U$13, U$14, U$15, U$16, U$17, U$18, U$19, U$20, U$21, U$22, U$23, U$24, U$25: MOSFET-N_LFPAK33; SOT1210
VRAW_TEST: PINHD-1X2NOSILK; 1X02_NOSILK

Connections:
32KHZ: ATMEGA328P.7 (PB6(XTAL1/TOSC1)), DS3231M.1 (P$1_32KHZ), R5.1
ANALOG_0: ADG725B.41 (DB), ATMEGA328P.23 (PC0(ADC0)), C14.1
AREF: ADG725B.43 (DA), AREF.1, ATMEGA328P.20 (AREF), C10.2, C13.1, MAX6103.2 (REF_OUT)
AVCC: ATMEGA328P.18 (AVCC), C3.1, INDUCTOR.P$1 (1)
BATT_MONITOR: ATMEGA328P.22 (ADC7), R13.2, R14.1
BATT_MONITOR_EN: ATMEGA328P.2 (PD4(XCK/T0)), R9.2, R15.1
BLUELED: ATMEGA328P.10 (PD6(AIN0)), R11.2
BUTTON1: ATMEGA328P.32 (PD2(INT0)), BUTTON1.P$3 (S), BUTTON1.P$4 (S)
CS_MUX: ADG725B.17 (!SYNC), ATMEGA328P.11 (PD7(AIN1))
CS_SD: ATMEGA328P.14 (PB2(SS/OC1B)), U$2.CS2 (CS)
DTR: C2.1, FTDI.1
GND: ADG725B.23 (GND), ADG725B.24 (VSS), AP2204_VREG.P$2 (GND), ATMEGA328P.3 (GND), ATMEGA328P.5 (GND), ATMEGA328P.21 (AGND), BATT_INPUT1.P$2, BATT_INPUT2.P$2, BJT_NPN.2 (E), BUTTON1.P$1, BUTTON1.P$2, C1.2, C3.2, C4.2, C5.2, C6.2, C7.-, C8.2, C9.-, C10.1, C11.2, C12.2, C13.2, C14.2, DS3231M.5 (P$5_GND), FTDI.5, FTDI.6, ISP.6, MAX6103.3 (GND), MUSSEL1.P$2, MUSSEL2.P$2, MUSSEL3.P$2, MUSSEL4.P$2, MUSSEL5.P$2, MUSSEL6.P$2, MUSSEL7.P$2, MUSSEL8.P$2, MUSSEL9.P$2, MUSSEL10.P$2, MUSSEL11.P$2, MUSSEL12.P$2, MUSSEL13.P$2, MUSSEL14.P$2, MUSSEL15.P$2, MUSSEL16.P$2, OLED.GND, PCA9685.1 (A0), PCA9685.2 (A1), PCA9685.3 (A2), PCA9685.4 (A3), PCA9685.5 (A4), PCA9685.14 (GND), PCA9685.24 (A5), PCA9685.25 (EXTCLK), R14.2, R15.2, R18.2, R19.2, R20.2, R21.2, R22.2, R23.2, R24.2, R25.2, R26.2, R27.2, R28.2, R29.2, R30.2, R31.2, R32.2, R33.2, RESET.P$1, RESET.P$2, TC2030_ISP.6 (GND), TEMP17.P$2, TEMP18.P$2, TEMP19.P$2, TEMP20.P$2, U$2.GND6 (VSS_GND), U$2.MNT1 (GND1), U$2.MNT2 (GND2), U$2.MNT3 (GND3), U$2.MNT4 (GND4), U$5.GND, U$10.1 (S), U$10.2 (S), U$10.3 (S), U$11.1 (S), U$11.2 (S), U$11.3 (S), U$12.1 (S), U$12.2 (S), U$12.3 (S), U$13.1 (S), U$13.2 (S), U$13.3 (S), U$14.1 (S), U$14.2 (S), U$14.3 (S), U$15.1 (S), U$15.2 (S), U$15.3 (S), U$16.1 (S), U$16.2 (S), U$16.3 (S), U$17.1 (S), U$17.2 (S), U$17.3 (S), U$18.1 (S), U$18.2 (S), U$18.3 (S), U$19.1 (S), U$19.2 (S), U$19.3 (S), U$20.1 (S), U$20.2 (S), U$20.3 (S), U$21.1 (S), U$21.2 (S), U$21.3 (S), U$22.1 (S), U$22.2 (S), U$22.3 (S), U$23.1 (S), U$23.2 (S), U$23.3 (S), U$24.1 (S), U$24.2 (S), U$24.3 (S), U$25.1 (S), U$25.2 (S), U$25.3 (S), VRAW_TEST.2
GRNLED: ATMEGA328P.9 (PD5(T1)), R10.2
HEATER1_GND: MUSSEL1.P$4, U$11.MB (D)
HEATER2_GND: MUSSEL2.P$4, U$12.MB (D)
HEATER3_GND: MUSSEL3.P$4, U$13.MB (D)
HEATER4_GND: MUSSEL4.P$4, U$14.MB (D)
HEATER5_GND: MUSSEL5.P$4, U$15.MB (D)
HEATER6_GND: MUSSEL6.P$4, U$16.MB (D)
HEATER7_GND: MUSSEL7.P$4, U$17.MB (D)
HEATER8_GND: MUSSEL8.P$4, U$18.MB (D)
HEATER9_GND: MUSSEL9.P$4, U$19.MB (D)
HEATER10_GND: MUSSEL10.P$4, U$20.MB (D)
HEATER11_GND: MUSSEL11.P$4, U$21.MB (D)
HEATER12_GND: MUSSEL12.P$4, U$22.MB (D)
HEATER13_GND: MUSSEL13.P$4, U$23.MB (D)
HEATER14_GND: MUSSEL14.P$4, U$24.MB (D)
HEATER15_GND: MUSSEL15.P$4, U$25.MB (D)
HEATER16_GND: MUSSEL16.P$4, U$10.MB (D)
MAX_DATA: ATMEGA328P.12 (PB0(ICP)), R8.1, TEMP17.P$1, TEMP18.P$1, TEMP19.P$1, TEMP20.P$1
MISO: ATMEGA328P.16 (PB4(MISO)), ISP.1, TC2030_ISP.1 (MISO), U$2.MISO7 (DATA_OUT_MISO)
MOSI: ADG725B.18 (DIN), ATMEGA328P.15 (PB3(MOSI/OC2)), ISP.4, TC2030_ISP.4 (MOSI), U$2.MOSI3 (DATA_IN_MOSI)
unnamed: BATT_INPUT1.P$1, U$7.P$1 (A), U$7.P$2 (A)
unnamed: BATT_INPUT2.P$1, U$8.P$1 (A), U$8.P$2 (A)
unnamed: R7.1, U$2.NC1 (DAT1_NC)
unnamed: R6.1, U$2.RES8 (DAT2_RES)
unnamed: BJT_NPN.3 (C), MOSFET-P.1 (G), R16.2
unnamed: BJT_NPN.1 (B), R9.1
unnamed: ADG725B.12 (S1A), R34.2
unnamed: R12.1, RGB_LED.P$2
unnamed: R10.1, RGB_LED.P$3
unnamed: R11.1, RGB_LED.P$4
unnamed: MOSFET-P.3 (D), R13.1
unnamed: ADG725B.11 (S2A), R35.2
unnamed: ADG725B.10 (S3A), R36.2
unnamed: ADG725B.9 (S4A), R37.2
unnamed: ADG725B.8 (S5A), R38.2
unnamed: ADG725B.7 (S6A), R39.2
unnamed: ADG725B.6 (S7A), R40.2
unnamed: ADG725B.5 (S8A), R41.2
unnamed: ADG725B.4 (S9A), R42.2
unnamed: ADG725B.3 (S10A), R43.2
unnamed: ADG725B.2 (S11A), R44.2
unnamed: ADG725B.1 (S12A), R45.2
unnamed: ADG725B.48 (S13A), R46.2
unnamed: ADG725B.47 (S14A), R47.2
unnamed: ADG725B.46 (S15A), R48.2
unnamed: ADG725B.45 (S16A), R49.2
PC1: ATMEGA328P.24 (PC1(ADC1)), PC1.1
PC2: ATMEGA328P.25 (PC2(ADC2)), PC2.1
PWM1: PCA9685.6 (PWM0), R19.1, U$11.4 (G)
PWM2: PCA9685.7 (PWM1), R20.1, U$12.4 (G)
PWM3: PCA9685.8 (PWM2), R21.1, U$13.4 (G)
PWM4: PCA9685.9 (PWM3), R22.1, U$14.4 (G)
PWM5: PCA9685.10 (PWM4), R23.1, U$15.4 (G)
PWM6: PCA9685.11 (PWM5), R24.1, U$16.4 (G)
PWM7: PCA9685.12 (PWM6), R25.1, U$17.4 (G)
PWM8: PCA9685.13 (PWM7), R26.1, U$18.4 (G)
PWM9: PCA9685.15 (PWM8), R27.1, U$19.4 (G)
PWM10: PCA9685.16 (PWM9), R28.1, U$20.4 (G)
PWM11: PCA9685.17 (PWM10), R29.1, U$21.4 (G)
PWM12: PCA9685.18 (PWM11), R30.1, U$22.4 (G)
PWM13: PCA9685.19 (PWM12), R31.1, U$23.4 (G)
PWM14: PCA9685.20 (PWM13), R32.1, U$24.4 (G)
PWM15: PCA9685.21 (PWM14), R33.1, U$25.4 (G)
PWM16: PCA9685.22 (PWM15), R18.1, U$10.4 (G)
PWM_!OE: ATMEGA328P.1 (PD3(INT1)), PCA9685.23 (#OE)
REDLED: ATMEGA328P.13 (PB1(OC1A)), R12.2
RESET: ATMEGA328P.29 (PC6(/RESET)), C2.2, ISP.5, R4.1, RESET.P$3 (S), RESET.P$4 (S), TC2030_ISP.5 (RESET)
SCK: ADG725B.19 (SCLK), ATMEGA328P.17 (PB5(SCK)), ISP.3, TC2030_ISP.3 (SCK), U$2.SCK5 (SCLK)
SCL: ATMEGA328P.28 (PC5(ADC5/SCL)), DS3231M.8 (P$8_SCL), OLED.SCL, PCA9685.26 (SCL), R3.1
SDA: ATMEGA328P.27 (PC4(ADC4/SDA)), DS3231M.7 (P$7_SDA), OLED.SDA, PCA9685.27 (SDA), R2.1
THERM1: ADG725B.25 (S1B), MUSSEL1.P$3, R34.1
THERM2: ADG725B.26 (S2B), MUSSEL2.P$3, R35.1
THERM3: ADG725B.27 (S3B), MUSSEL3.P$3, R36.1
THERM4: ADG725B.28 (S4B), MUSSEL4.P$3, R37.1
THERM5: ADG725B.29 (S5B), MUSSEL5.P$3, R38.1
THERM6: ADG725B.30 (S6B), MUSSEL6.P$3, R39.1
THERM7: ADG725B.31 (S7B), MUSSEL7.P$3, R40.1
THERM8: ADG725B.32 (S8B), MUSSEL8.P$3, R41.1
THERM9: ADG725B.33 (S9B), MUSSEL9.P$3, R42.1
THERM10: ADG725B.34 (S10B), MUSSEL10.P$3, R43.1
THERM11: ADG725B.35 (S11B), MUSSEL11.P$3, R44.1
THERM12: ADG725B.36 (S12B), MUSSEL12.P$3, R45.1
THERM13: ADG725B.37 (S13B), MUSSEL13.P$3, R46.1
THERM14: ADG725B.38 (S14B), MUSSEL14.P$3, R47.1
THERM15: ADG725B.39 (S15B), MUSSEL15.P$3, R48.1
THERM16: ADG725B.40 (S16B), MUSSEL16.P$3, R49.1
TO_FTDI_RX: ATMEGA328P.31 (PD1(TXD)), FTDI.2
TO_FTDI_TX: ATMEGA328P.30 (PD0(RXD)), FTDI.3
VBAT: DS3231M.6 (P$6_VBAT), U$5.P$1 (VBAT), U$5.P$2 (VBAT)
VCC: ADG725B.13 (VDD), ADG725B.14 (VDD), AP2204_VREG.P$3 (VOUT), ATMEGA328P.4 (VCC), ATMEGA328P.6 (VCC), C1.1, C4.1, C5.1, C6.1, C7.+, C8.1, C11.1, C12.1, DS3231M.2 (P$2_VCC), FTDI.4, INDUCTOR.P$2 (2), ISP.2, MAX6103.1 (VIN), OLED.VCC, PCA9685.28 (VDD), R2.2, R3.2, R4.2, R5.2, R6.2, R7.2, R8.2, RGB_LED.P$1 (P$1_ANODE), TC2030_ISP.2 (VCC), TEMP17.P$4, TEMP18.P$4, TEMP19.P$4, TEMP20.P$4, U$2.VDD4 (VDD)
VRAW: AP2204_VREG.P$1 (VIN), C9.+, MOSFET-P.2 (S), MUSSEL1.P$1, MUSSEL2.P$1, MUSSEL3.P$1, MUSSEL4.P$1, MUSSEL5.P$1, MUSSEL6.P$1, MUSSEL7.P$1, MUSSEL8.P$1, MUSSEL9.P$1, MUSSEL10.P$1, MUSSEL11.P$1, MUSSEL12.P$1, MUSSEL13.P$1, MUSSEL14.P$1, MUSSEL15.P$1, MUSSEL16.P$1, R16.1, U$7.P$3 (C), U$8.P$3 (C), VRAW_TEST.1

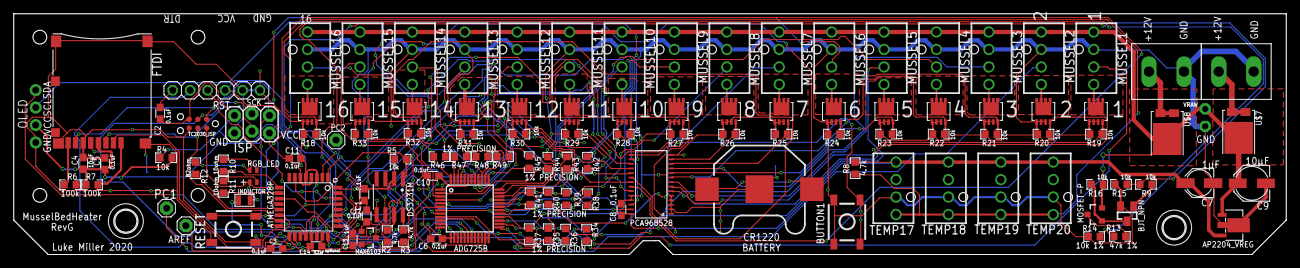
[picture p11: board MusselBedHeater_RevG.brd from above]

Board: 2 copper layers, 185.0 x 35.0 mm, 125 parts (0 on the bottom side), 103 nets.

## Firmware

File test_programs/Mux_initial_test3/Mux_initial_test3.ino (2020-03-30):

/*
 * Mux_initial_test3.ino
 * Luke Miller 2020
 * 
 * Testing with MusselBedHeater RevC hardware
 * Tested working for thermistor channel 1,2
 * 
 * Analog input on pin A0 (PC0)
 * ADG725 MUX SYNC pin connected to D7 (PD7)
 */

#include <SPI.h>
#include "MusselBedHeaterlib.h"

#define CS_MUX 7 // Arduino pin D7 connected to ADG725 SYNC pin
#define CS_SD 10 // Pin used for SD card
#define THERM A0 // Arduino analog input pin A0, reading thermistors from ADG725 mux
#define SPI_SPEED 4000000 // Desired SPI speed for talking to ADG725

ADG725 mux; // create ADG725 multiplexer object
uint8_t ADGchannel = 0x00; // initial value to activate ADG725 channel S1

void setup() {
  Serial.begin(57600);
  pinMode(CS_SD, OUTPUT); // declare as output so that SPI library plays nice
  pinMode(CS_MUX, OUTPUT); // Set CS_MUX pin as output for ADG725 SYNC
  pinMode(THERM, INPUT); // Analog input from ADG725
  
  SPI.begin();
  mux.begin(CS_MUX, SPI_SPEED); // Set up multiplexer
  mux.setADG725channel(ADGchannel); // Activate channel stored in ADGchannel variable
}

void loop() {
  delay(100);
  unsigned int thermRaw = analogRead(THERM);
  Serial.println(thermRaw);

}

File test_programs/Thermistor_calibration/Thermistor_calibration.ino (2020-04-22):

/*
 * Thermistor_calibration.ino
 * Luke Miller 2020
 * 
 * Use this sketch to display temperature data for MAX31820 sensors
 * and up to 16 thermistors (the MAX31820s can serve as references).
 * 
 * Testing with MusselBedHeater RevC hardware

 * 
 * Analog input on pin A0 (PC0) for thermistor voltages
 * ADG725 MUX SYNC pin connected to D7 (PD7)
 */

#include <SPI.h>
#include "NTC_Thermistor.h" // https://github.com/YuriiSalimov/NTC_Thermistor
#include "MusselBedHeaterlib.h" // https://github.com/millerlp/MusselBedHeaterlib

#define PLOTTER_OUTPUT 1 // Set 0 for Serial Monitor (text) output, 1 for plotter output
#define showRef false // Show reference mussel temperatures on Plotter output? true or false
#define CS_MUX 7 // Arduino pin D7 connected to ADG725 SYNC pin
#define CS_SD 10 // Pin used for SD card (not implemented here, but should be defined)
#define THERM A0 // Arduino analog input pin A0, reading thermistors from ADG725 mux
#define SPI_SPEED 4000000 // Desired SPI speed for talking to ADG725
// Thermistor library constants
#define REFERENCE_RESISTANCE  4700  // Specific to MusselBedHeater RevC on-board reference resistors
#define NOMINAL_RESISTANCE    6800  // Specific to MusselBedHeater RevC chosen thermistor
#define NOMINAL_TEMPERATURE   25
#define B_VALUE               4250  // Specific to MusselBedHeater RevC chosen thermistor
// Other thermistor-related constants
#define NUM_THERMISTORS       9  // Number of thermistors to sample
#define THERM_AVG             4   // Number of thermistor readings to average
#define TEMP_FILTER           2.0 // Threshold temperature change limit between readings


Thermistor* thermistor1;
ADG725 mux;
uint8_t ADGchannel = 0x00; // Initial value to activate ADG725 channel S1

double pidInput[16] = {}; // 16 position array of Input values for PID, this
                       // also serves as the current thermistor temperature
                       // readings array if you want to write these to disk

//--------- RGB LED setup --------------------------
// Create object for red green blue LED
RGBLED rgb;
//-------- timing ------------------
unsigned long prevMillis; // units of milliseconds
unsigned int sampleInterval = 500; // time between sampling events, units milliseconds
//----------------------------------------------------------
// OneWire MAX31820 temperature sensor macros and variables
// These are for the reference (unheated) mussels
#define ONE_WIRE_BUS 8  // Data pin for MAX31820s is D8 on MusselBedHeater RevC
#define TEMPERATURE_PRECISION 11 // 11-bit = 0.125C resolution
// Create a OneWire object called max31820 that we will use to communicate
OneWire max31820(ONE_WIRE_BUS); 
// Pass our OneWire reference to DallasTemperature library object.
DallasTemperature refSensors(&max31820);
uint8_t numRefSensors; // store number of available MAX31820 temperature sensors
// Array to store MAX31820 addresses, sized for max possible number of sensors, 
// each 8 bytes long
uint8_t sensorAddr[4][8] = {}; // Up to 4 MAX31820 sensors on MusselBedHeater RevC boards
uint8_t addr[8] = {};  // Address array for MAX31820, 8 bytes long
double avgMAXtemp = 0; // Average of MAX31820 sensors


//----------------------------------------------------------------
//------------- Setup loop ---------------------------------------
void setup() {
  Serial.begin(57600);
  pinMode(CS_SD, OUTPUT); // declare as output so that SPI library plays nice
  pinMode(CS_MUX, OUTPUT); // Set CS_MUX pin as output for ADG725 SYNC
  pinMode(THERM, INPUT); // Analog input from ADG725
  rgb.begin(); // Setup RGB with default pins (9,6,5)
  for (byte i = 0; i < 5; i++){
    rgb.setColor(0,100,0);
    delay(30);
    rgb.setColor(0,0,0);
    delay(30);    
  }



  // Set up thermistor1 object
  thermistor1 = new NTC_Thermistor(
    THERM,
    REFERENCE_RESISTANCE,
    NOMINAL_RESISTANCE,
    NOMINAL_TEMPERATURE,
    B_VALUE);
  // Initialize multiplexer object
  mux.begin(CS_MUX, SPI_SPEED);
  SPI.begin();
  // Get initial values from the thermistor(s)
  for (byte j = 0; j < 4; j++){
    for (byte i = 0; i < NUM_THERMISTORS; i++){
      mux.setADG725channel(ADGchannel | i); // Activate channel i 
      // Take an initial reading and throw it away (gives ADC time to settle)
      thermistor1 -> readCelsius();
      delay(1);
      // Take a reading from thermistor1
      pidInput[i] = thermistor1 -> readCelsius();
    }
  }
  // Turn off all multiplexer channels (shuts off thermistor circuits)
  mux.disableADG725(); 

  //---------- MAX31820 setup ---------------------------------
  // Start up the DallasTemperature library object
  refSensors.begin();
  numRefSensors = refSensors.getDeviceCount();
  // Call function from MusselBedHeaterlib library
  getRefSensorAddresses(max31820, refSensors, numRefSensors, sensorAddr); 
  for (byte i = 0; i < numRefSensors; i++){
    for (byte j = 0; j < 8; j++){
    }
  }
  // Set library to not wait for a conversion to complete after requesting temperatures
  // (Allows the program to do other things while MAX31820s are taking ~400ms to 
  // generate new temperature values)
  refSensors.setWaitForConversion(false);
  // Tell all MAX31820s to begin taking the first temperature readings
  refSensors.requestTemperatures();
  delay(500); // Let some time run after requesting temperatures


#if (PLOTTER_OUTPUT == 0) 
  // Serial monitor text output, no headers needed
#elif (PLOTTER_OUTPUT == 1)
  // Serial plotter output, print headers one time
    if (showRef) {
      Serial.print(F("AvgRefTemp,")); // Plot average MAX31820 temperature  
    }
    
    for (byte i = 0; i < NUM_THERMISTORS; i++){
      Serial.print(F("Ch"));
      Serial.print(i);
      Serial.print(",");
    }
    Serial.println();
#endif

  
}


//-------------- Main loop ----------------------------
void loop() {

  byte goodReadings = 0;
  double MAXTemps[numRefSensors] = {}; // MAX31820 temperature array
  unsigned long newMillis = millis();
  
  // If we've passed the sample interval time, take new readings
  if ( (newMillis - prevMillis) >= sampleInterval){
      prevMillis = newMillis; // Update prevMillis for next loop
      // Cycle through all MAX31820s and read their temps
      avgMAXtemp = 0; // Reset average temperature variable
      goodReadings = 0; // Reset goodReadings counter
      for (byte i = 0; i < numRefSensors; i++){
        //********** Faster version, using known addresses ********
        // Extract current device's 8-byte address from sensorAddr array
        for (int n = 0; n < 8; n++){
          addr[n] = sensorAddr[i][n];
        }
        MAXTemps[i] = refSensors.getTempC(addr); // query using device address

        // Sanity check the recorded temperature
        if ( (MAXTemps[i] > -10.0) & (MAXTemps[i] < 60.0) ){
          avgMAXtemp = avgMAXtemp + MAXTemps[i];
          goodReadings = goodReadings + 1;   
        }
        
      }
      
      // Start the next temperature reading
      refSensors.requestTemperatures();
      // Calculate average MAX31820 temperature of reference mussels
      avgMAXtemp = avgMAXtemp / (double)goodReadings; 
    
      //------------ Thermistor readings --------------
      // Read the thermistor(s)
      for (byte i = 0; i < NUM_THERMISTORS; i++){
        mux.setADG725channel(ADGchannel | i); // Activate channel i
        // Take an initial reading and throw it away (gives ADC time to settle)
        thermistor1 -> readCelsius();
        delay(2); 
        double tempVal = 0;
        double thermAvg = 0;
        goodReadings = 0; // Reset goodReadings counter
        // Take THERM_AVG number of successive readings from this thermistor
        // and average them together, along with checking and removing 
        // spurious temperature spikes
        for (byte j = 0; j < THERM_AVG; j++){
          // Take the temperature reading
          tempVal = thermistor1 -> readCelsius();
          // Check the temperature reading relative to previous step's temperature value
          // I was getting spurious temperature spikes (high and low) in excess of 2-3C every
          // 10-30 seconds, which really threw off the PID routine. This filtering below 
          // just throws out temperatures that change too much in the ~500ms between loops
          if (pidInput[i] > -100) {
            // If previous pidInput temperature was reasonable, use it to 
            // filter out spurious large changes in temperature readings
           if ( abs(tempVal - pidInput[i]) < TEMP_FILTER ){
              // Value is probably good
              thermAvg += tempVal;
              goodReadings = goodReadings + 1;
           }           
          } else {
              // If previous pidInput was questionable, just get a set of temps
              thermAvg += tempVal;
              goodReadings = goodReadings + 1;
          }
        }
        // Calculate an average temperature from the good readings
        pidInput[i] = thermAvg / (double)goodReadings;
      }
      // Turn off all multiplexer channels (shuts off thermistor circuits)
      mux.disableADG725(); 
      //----------------------------
      // Output block
#if (PLOTTER_OUTPUT == 0) 
    // Code for Serial monitor text output 
    // Print individual MAX31820 sensor values
    for (byte i = 0; i < numRefSensors; i++){
      Serial.print(F("MAX"));
      Serial.print(i);
      Serial.print(F(":"));
      Serial.print(MAXTemps[i],2);
      Serial.print(F(" "));
    }
    // Print thermistor values
    for (byte i = 0; i < NUM_THERMISTORS; i++){
      Serial.print(F("T"));
      Serial.print(i);
      Serial.print(F(":"));
      Serial.print(pidInput[i],2);
      Serial.print(F("C "));  
    }
    Serial.println();
#elif (PLOTTER_OUTPUT == 1) 
    // Code for Serial plotter output
    if (showRef){
      Serial.print(avgMAXtemp,2); // Plot average MAX31820 temperature
      Serial.print(F("\t"));  
    }
    
    // Plot the individual thermistor temperatures
    for (byte i = 0; i < NUM_THERMISTORS; i++){
      if (pidInput[i] < 0){
        // If values show up as -273.15 (missing thermistor), set them to 0 for better plotting
        Serial.print(0.0);
      } else {
        Serial.print(pidInput[i]);
      }
      Serial.print(F("\t"));
    }
    Serial.println();
#endif
      

  } // End of temperature sampling routine



}

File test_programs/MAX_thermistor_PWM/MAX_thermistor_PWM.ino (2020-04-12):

/*
 * Basic working example, initializing multiple MAX31820s
 * and reading them back using MusselBedHeaterlib library,
 * along with reading thermistors and doing multiple PID calculations 
 * 
 * TODO: Set up multiple PID objects to handle 16 thermistor channels
 * TODO: Send PID outputs to PWM objects to turn on heater
 * TODO: Tune PID
 * TODO: Implement SD card file creation, data saving
 * TODO: Implement real time clock
 * TODO: Implement battery monitoring
 * TODO: Implement tide prediction routine
 * TODO: Set up state machine to only run heaters at low tide
 */
#include "SdFat.h" // https://github.com/greiman/SdFat
#include "OneWire.h"  // For MAX31820 temperature sensor https://github.com/PaulStoffregen/OneWire
#include "DallasTemperature.h" // For MAX31820 sensors https://github.com/milesburton/Arduino-Temperature-Control-Library
#include "NTC_Thermistor.h" // https://github.com/YuriiSalimov/NTC_Thermistor
//#include "PID_v1.h" // https://github.com/br3ttb/Arduino-PID-Library/
#include <Wire.h>
#include "RTClib.h" // https://github.com/millerlp/RTClib
#include "Adafruit_PWMServoDriver.h" // https://github.com/adafruit/Adafruit-PWM-Servo-Driver-Library
#include "MusselBedHeaterlib.h" // https://github.com/millerlp/MusselBedHeaterlib

double tempIncrease = 1.0; // Celsius, target temperature increase for heated 
                           // mussels relative to reference mussels
#define NUM_THERMISTORS 16 // Number of thermistor channels
//----------------------------------------------
// Multiplexer macros for use in reading thermistors in heated mussels
#define CS_MUX 7 // Arduino pin D7 connected to ADG725 SYNC pin
#define CS_SD 10 // Pin used for SD card
#define THERM A0 // Arduino analog input pin A0, reading thermistors from ADG725 mux
#define SPI_SPEED 4000000 // Desired SPI speed for talking to ADG725
// Create Thermistor object
Thermistor* thermistor1;
// Create multiplexer object
ADG725 mux; 
uint8_t ADGchannel = 0x00; // Initial value to activate ADG725 channel S1
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

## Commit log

2020-03-24 Basic working example
    Reading 2 sensors on RevC hardware
2020-03-25 Updated MAX31820 test sketch
    Reads from up to 4 MAX31820 devices on RevC hardware
2020-03-30 Working thermistor temperature
2020-04-04 Reading MAX and thermistors
    Need to implement multiple PIDs, and interface with PWM chip to manipulate heaters.
2020-04-10 Making some stuff into globals
    See Serial print statements at the bottom for the troubleshooting. Seems to be a minimal working example for one channel currently.
2020-04-10 Cleaning up arrays and globals
    Added variable to set targeted temperature increase over reference mussel temperature.
2020-04-14 Potentially working full prototype
    NEEDS TESTING - saves data to card, calculates tide etc. Need to tune PID routine, test battery monitoring, testing heating routine with working mussels, flash LEDs for status updates
2020-04-15 TODO: implement the temperature filtering
2020-04-19 Not tested - basic temp display
    Could be used to test thermistor calibration against the MAX31820 temperature sensors.
2020-04-22 Modifying thermistor read routine
    Adding some conditional if statements to make sure we can recover from a case where a thermistor goes offline temporarily and then starts working again.
2020-04-27 Creating this for heater project
2020-04-29 Setting additional pins appropriately
    Make sure the PWM chip output enable pin is set as an output, pulled low.
2020-07-06 Basic blink for 3-color RGB LED
2020-07-06 Use to check function of MAX31820 sensors
2020-07-06 new board
2020-07-10 Ignore, new boards
2020-07-27 testing battery monitor circuit
2020-07-27 Show MAX31820 temperatures
2020-07-27 Test run with 16 sensors
2021-04-26 New field version
    Multiple changes and a new file name:
    1. Fixed a probable bug in the STATE_IDLE transition to STATE_HEATING with a reversed < sign
    2. Adding output of predicted tide height and current program state to the SD card - NOTE: This also comes with a modification to the MusselBedHeaterlib library, so update that also
    3. Added continuous updating of pidSetpoint value when in STATE_OFF, since it wasn't doing that
2021-04-26 Adding decrement to lowVoltageCounter
    Trying to force the routine to only enter STATE_OFF if the battery voltage stays below the low voltage threshold for 5 consecutive minutes, instead of just hitting the low threshold 5 times total per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
2021-05-18 Working SD card test on 4809
    Must use current MegaCoreX (1.0.8) and SdFat-beta v2.1 to get this working.
2021-06-02 Making version of old RevC board
2021-06-07 Adding thermistor calibration correction
    Adding the variable therm_correction to allow for a manual correction of all of the recorded thermistor temperatures (one value applied to all 16 thermistors).
2021-07-19 Update for new board
2022-10-24 Latest hardware revision files
    [MusselBedHeater_RevG.brd, MusselBedHeater_RevG.sch]
2022-10-24 Parts lists updated 2022
    [MusselBedHeater_BOM.csv, MusselBedHeater_BOM.xlsx, MusselBedHeater_parts_list_RevG.csv]
2022-10-24 Heater coil board design
    [Heater_subassembly_revA.brd, Heater_subassembly_revA.sch]
2022-10-24 Heater coil info
2022-10-24 More description of the heater

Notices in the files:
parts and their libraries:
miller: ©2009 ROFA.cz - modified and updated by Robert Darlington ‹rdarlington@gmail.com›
